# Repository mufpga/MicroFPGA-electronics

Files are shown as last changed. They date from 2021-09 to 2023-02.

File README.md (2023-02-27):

<a href="https://mufpga.github.io/">Overview

</a>



# Overview

MicroFPGA is an FPGA-based platform for the electronic control of microscopes. It aims at using affordable FPGA to generate or read signals from a variety of devices, including cameras, lasers, servomotors, filter-wheels, etc. It can be controlled via [Micro-Manager](https://micro-manager.org/MicroFPGA), or its [Java](https://github.com/mufpga/MicroFPGA-java), [Python](https://github.com/mufpga/MicroFPGA-py) and [LabView](https://github.com/mufpga/MicroFPGA-labview) communication libraries, and comes with optional complementary [electronics](https://github.com/mufpga/MicroFPGA-electronics).

Documentation and tutorials are available on [https://mufpga.github.io/](https://mufpga.github.io/).

Overview

## Content

This repository contains the (optional) complementary electronics for MicroFPGA. Documentation for the electronics is available on the [project's website](https://mufpga.github.io/resource1_electronics.html) and in the papers.

Design files are available for the following elements:
- [Box](Box)
- [Box panel 1](Box_panel_1)
- [Box panel 2](Box_panel_2)
- [Box panel 3](Box_panel_3)
- [Analog conversion board (ACB)](Analog_conversion_board)
- [Signal conversion board (SCB)](Signal_conversion_board)
- [Custom FPGA shield](FPGA_shield)
- [Servo distribution board (SDB)](Servo_distribution_board)
- [AOTF conversion board (AOTF-CB)](AOTF_conversion_board)

## Cite us
Joran Deschamps, Christian Kieser, Philipp Hoess, Takahiro Deguchi, Jonas Ries, "MicroFPGA: An affordable FPGA platform for microscope control",
HardwareX 2023 (13): e00407, doi:[10.1016/j.ohx.2023.e00407](https://doi.org/10.1016/j.ohx.2023.e00407).

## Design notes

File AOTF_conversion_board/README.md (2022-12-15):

<a href="https://mufpga.github.io/">Overview

</a>



## Content

The AOTF conversion board takes two TTL inputs per channels:
1. Enable in: a TTL trigger such as the one generated by MicroFPGA laser triggers or a camera exposure signal.
2. PWM or DAQ (analog in): a PWM signal such as the one generated by MicroFPGA PWM signals, or an analog signal.

The PWM signal is low-passed and the resulting analog output is multiplied by the TTL signal. The resulting output is a 10 V analog signal that can be synchronized with a camera, and whose level is adjusted by changing the PWM input duty cycle. The output of the board is either 0-5V or 0-10V depending on the channel.

We used this board in addition to our electronics box in order to control AOTF/AOM, for instance with DPSS lasers.

- [Altium project](Altium_project)
- [Bill of materials](BOM)
- [Gerber files](Gerber)
- [Drill instructions](NC_Drill)

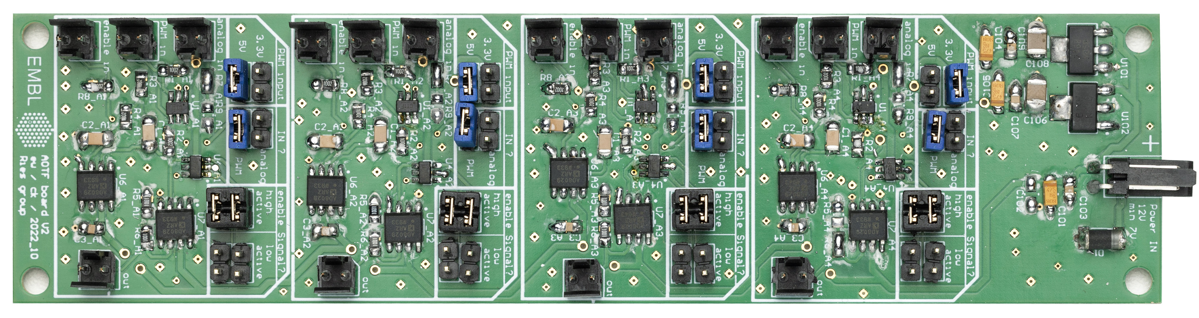
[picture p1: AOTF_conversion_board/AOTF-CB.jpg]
AOTF-CB


## Channel configuration

### Inputs
- _analog in_: analog signal that can be switched on or of by the _enable in_ signal.
- _PWM in_: PWM signal, which will be low-pass filtered by the board to generate an analog signal.
- _enable in_: TTL signal used to switch on and off the analog signal (_analog in_ or low-pass filtered _PWM in_)

> __Important__: inputs are either the analog or the PWM in, but not both simultaneously.
> Note: If you do not use the TTL input, you can set the _Enable signal ?_ to _low active_ in order to simply produce an analog signal.

### Ouput
- _out_: analog signal switched on/off following the TTL input.

### Settings
- _PWM input_: voltage of the PWM input (if applicable).
- _IN ?_: whether the input is _analog in_ or _PWM in_
- _Enable signal ?_: whether the analog output is switched on on _HIGH_ or _LOW_ TTL.

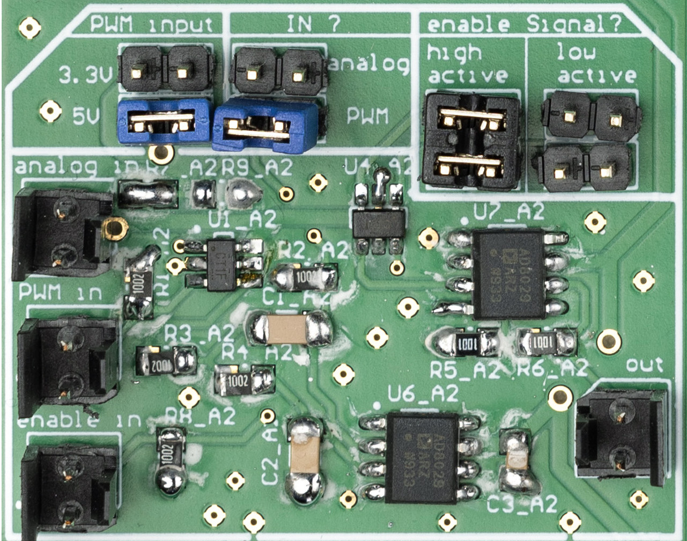
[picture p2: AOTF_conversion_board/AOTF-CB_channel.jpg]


Photography credit: EMBL Photolab - Stuart Ingham.

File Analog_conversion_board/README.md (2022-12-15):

<a href="https://mufpga.github.io/">Overview

</a>



## Content

The analog conversion board (ACB) scales down analog voltages from the ranges 0-10 V or 0-5 V to 0-1 V, in order to measure signals with the Au+ FPGA.

- [Altium project](Altium_project)
- [Bill of materials](BOM)
- [Gerber files](Gerber)
- [Drill instructions](NC_Drill)

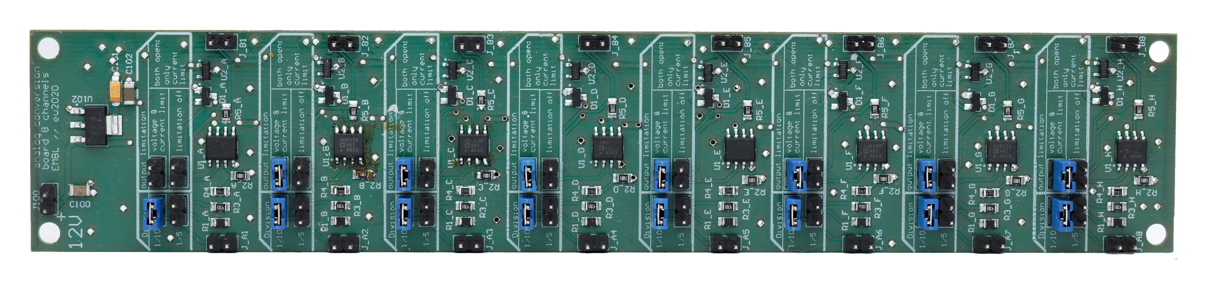
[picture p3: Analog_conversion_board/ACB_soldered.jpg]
ACB


## Channel configuration

### Input
- analog signal in the range 0-10V or 0-5V.

### Output
- analog signal in the range 0-1V.

### Settings
- _Division_: whether the input analog signal is 0-10V (1/10) or 0-5V (1/5), the output of the board is 0-1V.
- _output limitation_:
  - _voltage and current limitations_: limits both voltage and current to prevent damaging the FPGA ADC.
  - _limitations off_: the output voltage and current are not limited.
  - both open, only current limitation.

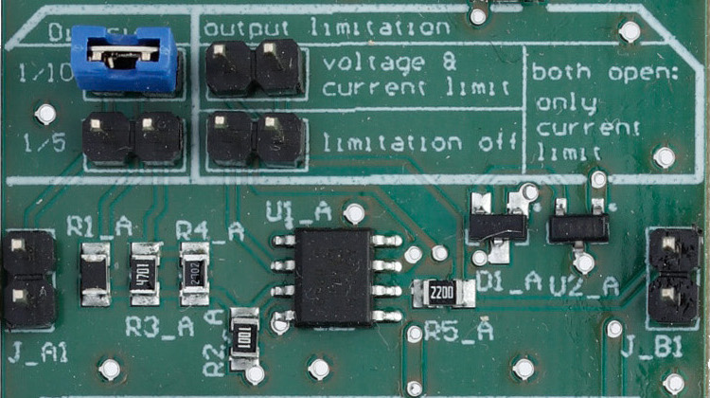
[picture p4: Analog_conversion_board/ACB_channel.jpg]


Photography credit: EMBL Photolab - Stuart Ingham.

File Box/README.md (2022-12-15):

<a href="https://mufpga.github.io/">Overview

</a>



## Content

The electronics box packages the different boards into a neat box with standard connectors. It is 3D printed and the lid machined from transparent plastic.

- [Bill of materials](BOM)
- [Build up pictures](Build_up)
- [CAD files](CAD_files)

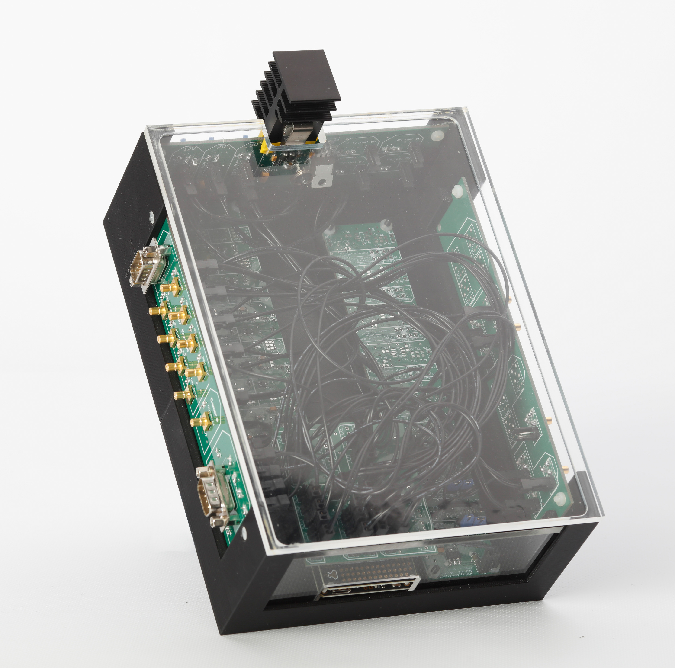
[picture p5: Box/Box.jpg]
Electronics box


Photography credit: EMBL Photolab - Stuart Ingham.

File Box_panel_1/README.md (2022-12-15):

<a href="https://mufpga.github.io/">Overview

</a>



## Content

The first box panel is connected to the laser (DO:LX:EN) and PWM signals (DO:LX:POW), as well as camera trigger input and the servos. The lasers outputs can be used directly to trigger diode lasers. The servo DSUB9 is connected to the [servo distribution board (SDB)](https://github.com/mufpga/MicroFPGA-electronics/tree/main/Servo_distribution_board). The other DSUB9 connector can be used with the [LaserEngine](https://github.com/ries-lab/LaserEngine) electronics. Finally, both laser and PWM signals could be used as inputs to the [AOTF conversion board (AOTF-CB)](https://github.com/mufpga/MicroFPGA-electronics/tree/main/AOTF_conversion_board) in order to control an AOTF or an AOM.

- [Altium project](Altium_project)
- [Bill of materials](BOM)
- [Gerber files](Gerber)
- [Drill instructions](NC_Drill)

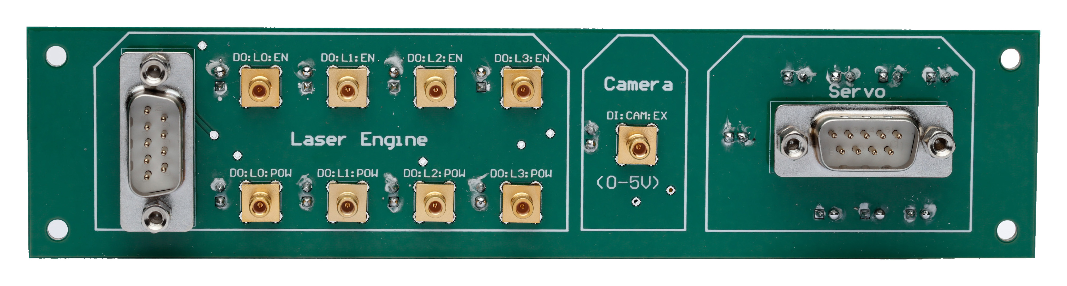
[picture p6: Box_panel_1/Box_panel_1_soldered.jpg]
Box panel 1


Photography credit: EMBL Photolab - Stuart Ingham.

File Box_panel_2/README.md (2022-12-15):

<a href="https://mufpga.github.io/">Overview

</a>



## Content

The second box panel is connected to AU+ analog inputs (in the case of the Cu FPGA, then these can be adapted for other outputs). It is also wired to the TTL outputs and the camera trigger output.

- [Altium project](Altium_project)
- [Bill of materials](BOM)
- [Gerber files](Gerber)
- [Drill instructions](NC_Drill)

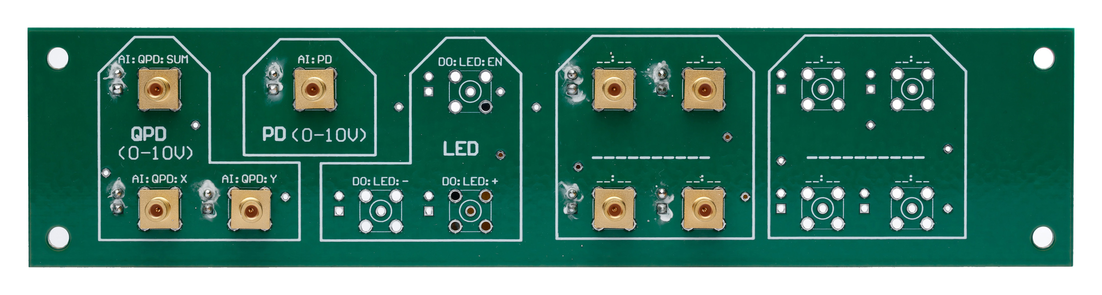
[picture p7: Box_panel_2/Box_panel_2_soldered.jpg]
Box panel 2


Photography credit: EMBL Photolab - Stuart Ingham.

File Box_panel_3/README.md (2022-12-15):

<a href="https://mufpga.github.io/">Overview

</a>



## Content

The third box panel is connected to the main power source and powers the other boards using different voltages.

- [Altium project](Altium_project)
- [Bill of materials](BOM)
- [Gerber files](Gerber)
- [Drill instructions](NC_Drill)

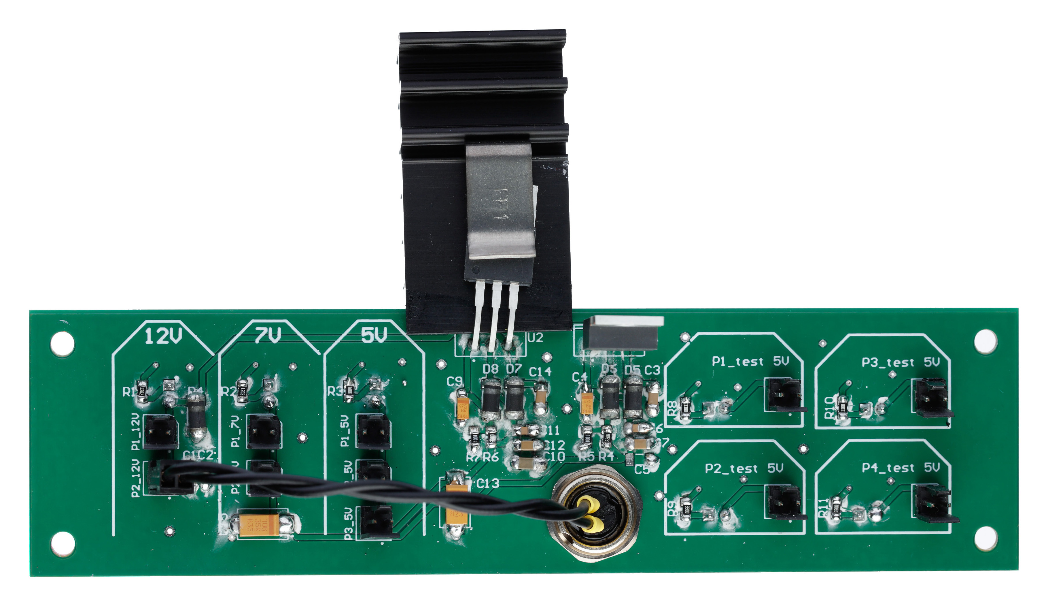
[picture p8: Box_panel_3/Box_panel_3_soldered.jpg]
Box panel 3


Photography credit: EMBL Photolab - Stuart Ingham.

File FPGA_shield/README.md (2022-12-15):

<a href="https://mufpga.github.io/">Overview

</a>



## Content

The custom FPGA shield can be plugged directly onto the Br shield (Alchitry) and facilitates the internal wiring of the electronics 
box. It features all the default inputs of MicroFPGA. Note that we prefer stacking it on top of the Br shield to avoid damaging the 
FPGA connectors and grant access to other FPGA pins that are unused by the custom shield.

- [Altium project](Altium_project)
- [Bill of materials](BOM)
- [Gerber files](Gerber)
- [Drill instructions](NC_Drill)

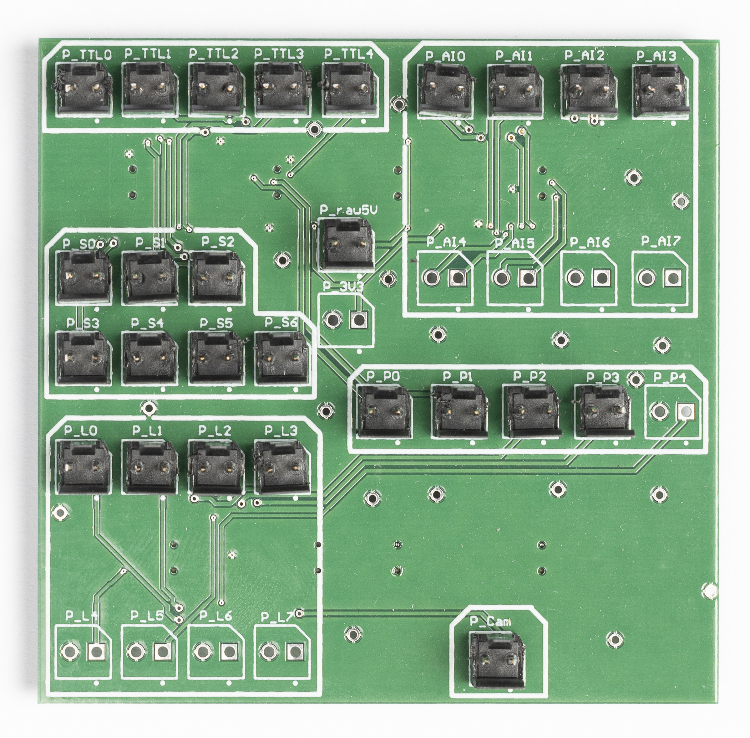
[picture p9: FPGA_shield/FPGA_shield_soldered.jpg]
Custom FPGA shield


Photography credit: EMBL Photolab - Stuart Ingham.

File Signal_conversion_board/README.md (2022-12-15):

<a href="https://mufpga.github.io/">Overview

</a>



## Content

The signal conversion board (SCB) features multiple bi-directional channels that scale up or down voltages in order to ensure compatibility
between the FPGA and devices connected to the electronics box. Two channels also include the possibility to low pass the PWM signals 
from MicroFPGA to produce analog voltage ouputs.

- [Altium project](Altium_project)
- [Bill of materials](BOM)
- [Gerber files](Gerber)
- [Drill instructions](NC_Drill)

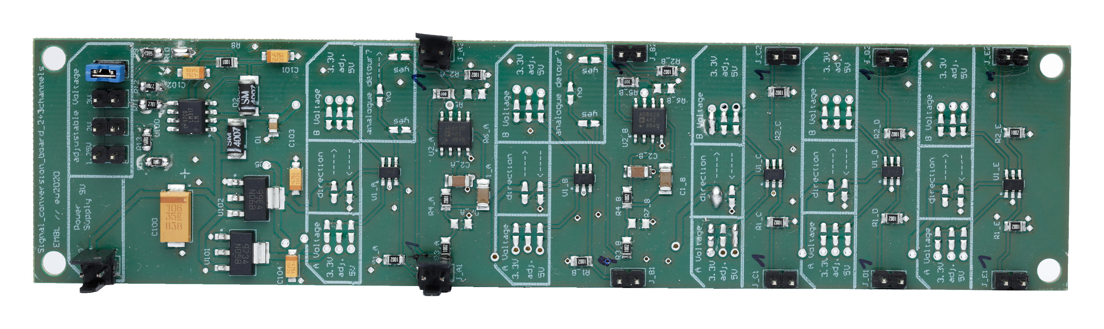
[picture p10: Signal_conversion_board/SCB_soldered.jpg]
SCB


## Channel configuration

Signal A on the left-hand side, signal B on the right-hand side.

### Input
- Digital signal (in A or B).

### Output
- Rescaled digital (in A or B) or analog signal (B).

### Settings
- _A voltage_: left-hand side voltage, where _adj_ is the adjustable voltage at the top of the board.
- _direction_: voltage conversion from left to right or right to left.
- _B voltage_: right-hand side voltage, where _adj_ is the adjustable voltage at the top of the board.
- _analogue detour_: whether to low pass A to produce an analog signal in B.
  
 > __Important__: digital to analog conversion (low-pass filter) only happens from A to B, from left to right.

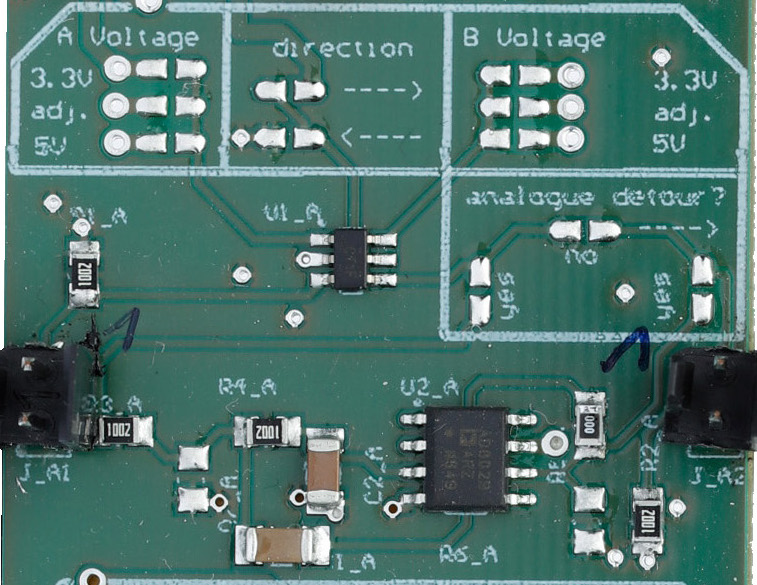
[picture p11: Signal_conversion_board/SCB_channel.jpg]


Photography credit: EMBL Photolab - Stuart Ingham.

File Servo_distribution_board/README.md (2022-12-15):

<a href="https://mufpga.github.io/">Overview

</a>



## Content

The servomotor distribution board (SDB) is intended to be a hub for servomotor cables. Placed in the center of the microscope, we use it to drive several servomotors (back-focal plane lens, 3D lens, filter wheels etc.), such as [the elements presented here](https://github.com/ries-lab/RiesPieces/tree/master/Microscopy). The flat cable from the DSUB9 is connected directly to the electronics box. It is simply screwed on a plastic board.

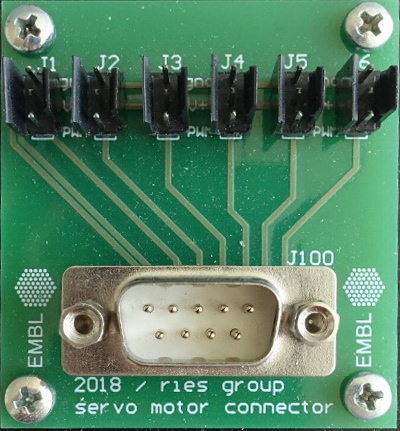
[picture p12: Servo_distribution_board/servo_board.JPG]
servomotor board


The project contains the following items:

- [Altium project](Altium_project)
- [Gerber files](Gerber)
- [Drill instructions](NC_Drill)

The board was designed by Ulf Matti (Ries lab, EMBL).

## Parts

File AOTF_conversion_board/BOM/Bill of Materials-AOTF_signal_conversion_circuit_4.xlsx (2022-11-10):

Line # | Name | Description | Designator | Revision ID | Quantity | Supplier | Supplier Part Number | PartNumber | Manufacturer
 | 61300211121 | 2Pol; gerade; WR-PHD 2.54 mm THT Pin Header | J1_A1, J1_A2, J1_A3, J1_A4, J2_A1, J2_A2, J2_A3, J2_A4, J3_A1, J3_A2, J3_A3, J3_A4, J4_A1, J4_A2, J4_A3, J4_A4, J5_A1, J5_A2, J5_A3, J5_A4, J6_A1, J6_A2, J6_A3, J6_A4, J7_A1, J7_A2, J7_A3, J7_A4, J8_A1, J8_A2, J8_A3, J8_A4 | CMP-001-0071-1 | 32 | Mouser | 710-61300211121 | 61300211121 | Wurth Electronics
 | 4,7 µF | 4,7 µF; 6V; Gr. A; T491A475K006AT | C101, C102, C104, C105 | CMP-001-0039-3 | 4 | Digi-Key | 399-9717-1-ND | T491A475K006AT | KEMET
 | LM1117IMP-3.3/NOPB | 800mA Low-Dropout Linear Regulator, 4-pin SOT-223, Pb-Free | U101 | CMP-00484-1 | 1 |  |  | LM1117IMP-3.3/NOPB | Texas Instruments
 | LM1117IMP-5.0/NOPB | 800mA Low-Dropout Linear Regulator, 4-pin SOT-223, Pb-Free | U102 | CMP-00485-1 | 1 |  |  | LM1117IMP-5.0/NOPB | Texas Instruments
 | SN74LVC1G3157 | Analoger Schalter Single SPDT(Wechsler) SOT23-6 | U4_A1, U4_A2, U4_A3, U4_A4 | CMP-001-0106-A.1 | 4 | Digi-Key | 74LVC1G3157DBVRE4-ND | SN74LVC1G3157DBVR | Texas Instruments
 | 885012208013 | CAP CER 1UF 10V X7R 1206 | C1_A1, C1_A2, C1_A3, C1_A4, C2_A1, C2_A2, C2_A3, C2_A4 | CMP-001-0138-A.1 | 8 | Digi-Key | 732-7685-1-ND | 885012208013 | Wurth Electronics Inc.
 | 100uF 6.3V 1210 | Ceramic Capacitor, Ceramic, 100uF, 6.3V | C106, C108 | CMP-001-0186-3 | 2 |  |  | 885012109004 | Wurth Electronics
 | 66100211722 | Intercom Male Shrouded Locking Header WR-WTB, THT, Right Angled, pitch 2.54 mm, 1 x 2 position | J100 | CMP-00524-A.1 | 1 |  |  | 66100211722 | Wurth Elektronik
 | LL4007 | LL4007; Vf 1,1V @ 1A, If = 1A | D1 | CMP-001-0049-2 | 1 | Farnell | 2677381 | LL4007G | TAIWAN SEMICONDUCTOR
 | AD8029ARZ | Single Channel RRIO Operational Amplifier, 125 MHz BW, 62 V/us SR, Industrial, 8-pin SOIC (R-8), Tube | U6_A1, U6_A2, U6_A3, U6_A4, U7_A1, U7_A2, U7_A3, U7_A4 | CMP-00480-1 | 8 |  |  | AD8029ARZ | Analog Devices
 | SN74LVC1T45DBVT | Single-Bit Dual-Supply Bus Transceiver with Configurable Voltage Translation and 3-State Outputs, DBV0006A, SMALL T&R | U1_A1, U1_A2, U1_A3, U1_A4 | CMP-00491-1 | 4 |  |  | SN74LVC1T45DBVT | Texas Instruments
 | 66100211622 | WR-WTB 2.54 mm Male Vertical Shrouded Header 2 Pins | J_A1, J_A2, J_A3, J_A4, J_B1, J_B2, J_B3, J_B4, J_C1, J_C2, J_C3, J_C4, J_D1, J_D2, J_D3, J_D4 | CMP-001-0161-A.3 | 16 | Digi-Key | 732-14102-ND | 66100211622 | Wurth Electronics
 |  | Generic parts with the format 0805 like resistances and capacities are not listed here!!.

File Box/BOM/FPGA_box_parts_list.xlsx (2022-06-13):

name | producer & producer parts number | Distributor | order number |  | amount | comment
board content of FPGA box:
Alchitry Au FPGA DEV-16527 | SparkFun DEV-16527 | mouser | 474-DEV-16527 |  | 1
Alchitry Br prototype shield | SparkFun DEV-16524 | mouser | 474-DEV-16524 |  | 1
boards pre assembled from company:
analog_conversion_board_8channels | Sigmann electronic Angebot: 2020-30170 |  |  | 197,14€ for 1pc 130,82€ each for min. 5pc 110,40€ each for min. 10pc | 1
signal_conversion_board_2+3channels | Sigmann electronic Angebot: 2020-30170 |  |  | 132,59€ for 1pc 67,28€ each for min. 5pc 51,41€ each for min. 10pc | 1
boards self-assembled:
FPGA_Au_shield | Q-print ----- |  |  | not assembled ordered | 1
FPGA_Frontpanel_1_V2 | Q-print ----- |  |  | not assembled ordered | 1
FPGA_Frontpanel_2_V1 | Q-print ----- |  |  | not assembled ordered | 1
FPGA_Frontpanel_3_V1 | Q-print ----- |  |  | not assembled ordered | 1
power supply
Mean Well Steckernetzteil Universal 12V dc / 1.5A, 18W | Mean Well GSM18E12-P1J | RS | 791-0913 |  | 1
cable connector 2 pole | Binder 99 0402 00 02 | Farnell | 1122556 |  | 1
box connector 2 pole | Binder 09 0403 00 02 | Farnell | 1122562 |  | 1
Box build up
spacing bolts, plastic, internal-|external-, M3 | M3, 10 mm long and 8mm outside |  | Bürklin | 18H3683 |  | 8 | beneath ACB and SCB boards
spacing bolts, metal, internal-|internal-, M2 | M2, 15 mm long |  | Bürklin | 18H2408 |  | 3 | beneath FPGA board
M4 nuts for distance holding |  |  |  |  | 3 | beneath FPGA board
M2 metal screws 10mm long with countersunk head |  |  |  |  | 3 | for FPGA board
M2 metal screws 12mm long with flat head |  |  |  |  | 3 | for FPGA board
M3 (plastic) screws 10mm long with countersunk head |  |  |  |  | 14 | for ACB/SCB and frontpanels
M3 (plastic) nut |  |  |  |  | 14 | for ACB/SCB and frontpanels
heat sink | Fischerelektronik THFU 1 | RS | 722-6921 |  | 1
heat sink clip | Fischerelektronik SK 481/25 SA | RS | 722-6886 |  | 1
2 x 1 PINS Multi-Jumper | Wuerth Electronic 60900213621 | Wuerth Electronic | 60900213621 |  | 16 | jumpers for the ACB board
WR-WTB from würth electronic prefabricated cables for wiring the boards
2 Pins | würth electronic | 661002113322 |  |  | 54 | current need but it depends on amount of signals needed
30cm both ends crimped | würth electronic | 661161122030 |  |  | 44 | current need but it depends on amount of signals needed

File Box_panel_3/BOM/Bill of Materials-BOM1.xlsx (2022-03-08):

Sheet: BOM Report
BOM Beta LAYOUT GmbH
 |  |  | Bill of Materials for BOM Document [BOM1.BomDoc]
Source Data From: |  | BOM1.BomDoc
Project: |  | FPGA_Frontpanel_3_V1.PrjPcb
Variant: |  | None
Creation Date: | 27.09.2021
Print Date: | 2021-09-27 | 44466.65563
Production Quantity: | 1
 |  |  |  |  |  |  |  |  |  |  |  | D | E | L |  | E | T | E
Designator | Name | LibRef | Footprint | Description | Quantity | Place YES / NO | Provided by Customer YES / NO | Supplier | Supplier Part Number | Manufacturer | PartNumber | Supplier 1 | Supplier Stock 1 | Supplier Part Number 1 | Supplier Order Qty 1 | Supplier Unit Price 1 | #Column Name Error:' Supplier 2 | #Column Name Error:' Supplier Stock 2 | #Column Name Error:' Supplier Part Number 2 | #Column Name Error:' Supplier Order Qty 2 | #Column Name Error:' Supplier Unit Price 2 | #Column Name Error:' Supplier 3 | #Column Name Error:' Supplier Stock 3 | #Column Name Error:' Supplier Part Number 3 | #Column Name Error:' Supplier Order Qty 3 | #Column Name Error:' Supplier Unit Price 3
J1 | 61300211121 | CMP-001-0071-2 | 61300211121 | 2Pol; gerade; WR-PHD 2.54 mm THT Pin Header | 1 | YES | NO | Mouser | 710-61300211121 | Wurth Electronics | 61300211121 | Mouser | 58866 | 710-61300211121 | 7 | 0.11
J2 | 61300211121 | CMP-001-0071-2 | 61300211121 | 2Pol; gerade; WR-PHD 2.54 mm THT Pin Header | 1 | YES | NO | Mouser | 710-61300211121 | Wurth Electronics | 61300211121 | Mouser | 58866 | 710-61300211121 | 7 | 0.11
J3 | 61300211121 | CMP-001-0071-2 | 61300211121 | 2Pol; gerade; WR-PHD 2.54 mm THT Pin Header | 1 | YES | NO | Mouser | 710-61300211121 | Wurth Electronics | 61300211121 | Mouser | 58866 | 710-61300211121 | 7 | 0.11
J4 | 61300211121 | CMP-001-0071-2 | 61300211121 | 2Pol; gerade; WR-PHD 2.54 mm THT Pin Header | 1 | YES | NO | Mouser | 710-61300211121 | Wurth Electronics | 61300211121 | Mouser | 58866 | 710-61300211121 | 7 | 0.11
J5 | 61300211121 | CMP-001-0071-2 | 61300211121 | 2Pol; gerade; WR-PHD 2.54 mm THT Pin Header | 1 | YES | NO | Mouser | 710-61300211121 | Wurth Electronics | 61300211121 | Mouser | 58866 | 710-61300211121 | 7 | 0.11
J6 | 61300211121 | CMP-001-0071-2 | 61300211121 | 2Pol; gerade; WR-PHD 2.54 mm THT Pin Header | 1 | YES | NO | Mouser | 710-61300211121 | Wurth Electronics | 61300211121 | Mouser | 58866 | 710-61300211121 | 7 | 0.11
J7 | 61300211121 | CMP-001-0071-2 | 61300211121 | 2Pol; gerade; WR-PHD 2.54 mm THT Pin Header | 1 | YES | NO | Mouser | 710-61300211121 | Wurth Electronics | 61300211121 | Mouser | 58866 | 710-61300211121 | 7 | 0.11
U1 | LM317AT/NOPB | CMP-00535-1 | NDE0003A | 3-Terminal Adjustable Regulator, 3-pin TO-220, Pb-Free | 1 | YES | NO |  |  | Texas Instruments |  | Mouser | 154 | 926-LM317AT/NOPB | 2 | 1.72
U2 | LM317AT/NOPB | CMP-00535-1 | NDE0003A | 3-Terminal Adjustable Regulator, 3-pin TO-220, Pb-Free | 1 | YES | NO |  |  | Texas Instruments |  | Mouser | 154 | 926-LM317AT/NOPB | 2 | 1.72
C4 | 4,7 µF | CMP-001-0039-5 | A Package | 4,7 µF; 6V; Gr. A; T491A475K006AT | 1 | YES | NO | Digi-Key | 399-9717-1-ND | KEMET | T491A475K006AT | Distrelec | 0 | 16771162 | 1 | 3.49
C9 | 4,7 µF | CMP-001-0039-3 | A Package | 4,7 µF; 6V; Gr. A; T491A475K006AT | 1 | YES | NO | Digi-Key | 399-9717-1-ND | KEMET | T491A475K006AT | Distrelec | 0 | 16771162 | 1 | 4.09
C13 | 10 µF | CMP-001-0033-3 | KEMT-520-D_Low | 10 µF, 35V, 125 mOhm, Gr. D partnumb: T495D106K035ATE125 | 1 | YES | NO | Digi-Key | 399-10292-1-ND | KEMET | T495D106K035ATE125 | Farnell | 441 | 2524590 | 2 | 3.5
C15 | 10 µF | CMP-001-0033-3 | KEMT-520-D_Low | 10 µF, 35V, 125 mOhm, Gr. D partnumb: T495D106K035ATE125 | 1 | YES | NO | Digi-Key | 399-10292-1-ND | KEMET | T495D106K035ATE125 | Farnell | 441 | 2524590 | 2 | 3.5
R1 | 805 | CMP-001-0027-2 | YAGO-RC0805_M | 0805 Yageo Standard BlackBox Resistors | 1 | YES | NO |  |  | Yageo
R2 | 805 | CMP-001-0027-2 | YAGO-RC0805_M | 0805 Yageo Standard BlackBox Resistors | 1 | YES | NO |  |  | Yageo
R3 | 805 | CMP-001-0027-2 | YAGO-RC0805_M | 0805 Yageo Standard BlackBox Resistors | 1 | YES | NO |  |  | Yageo
R4 | 805 | CMP-001-0027-2 | YAGO-RC0805_M | 0805 Yageo Standard BlackBox Resistors | 1 | YES | NO |  |  | Yageo
R5 | 805 | CMP-001-0027-2 | YAGO-RC0805_M | 0805 Yageo Standard BlackBox Resistors | 1 | YES | NO |  |  | Yageo
R6 | 805 | CMP-001-0027-2 | YAGO-RC0805_M | 0805 Yageo Standard BlackBox Resistors | 1 | YES | NO |  |  | Yageo
R7 | 805 | CMP-001-0027-2 | YAGO-RC0805_M | 0805 Yageo Standard BlackBox Resistors | 1 | YES | NO |  |  | Yageo
R8 | 805 | CMP-001-0027-2 | YAGO-RC0805_M | 0805 Yageo Standard BlackBox Resistors | 1 | YES | NO |  |  | Yageo
R9 | 805 | CMP-001-0027-2 | YAGO-RC0805_M | 0805 Yageo Standard BlackBox Resistors | 1 | YES | NO |  |  | Yageo
R10 | 805 | CMP-001-0027-2 | YAGO-RC0805_M | 0805 Yageo Standard BlackBox Resistors | 1 | YES | NO |  |  | Yageo
R11 | 805 | CMP-001-0027-2 | YAGO-RC0805_M | 0805 Yageo Standard BlackBox Resistors | 1 | YES | NO |  |  | Yageo
C3 | CAP 10uF 25V 1206(3216) | CMP-00471-2 | CAPC1206(3216)190_N | CAP 10uF 25V -20% to +80% 1206 (3216 Metric) Thickness 1.9mm SMD | 1 | YES | NO | Digi-Key | 732-7574-2-ND | Wurth Electronics Inc. | 885 012 208 069 | RSComponents | 25 | 1813519 | 25 | 0.54732
C5 | CAP 10uF 25V 1206(3216) | CMP-00471-2 | CAPC1206(3216)190_N | CAP 10uF 25V -20% to +80% 1206 (3216 Metric) Thickness 1.9mm SMD | 1 | YES | NO | Digi-Key | 732-7574-2-ND | Wurth Electronics Inc. | 885 012 208 069 | RSComponents | 25 | 1813519 | 25 | 0.54732
C10 | CAP 10uF 25V 1206(3216) | CMP-00471-2 | CAPC1206(3216)190_N | CAP 10uF 25V -20% to +80% 1206 (3216 Metric) Thickness 1.9mm SMD | 1 | YES | NO | Digi-Key | 732-7574-2-ND | Wurth Electronics Inc. | 885 012 208 069 | RSComponents | 25 | 1813519 | 25 | 0.54732
C14 | CAP 10uF 25V 1206(3216) | CMP-00471-2 | CAPC1206(3216)190_N | CAP 10uF 25V -20% to +80% 1206 (3216 Metric) Thickness 1.9mm SMD | 1 | YES | NO | Digi-Key | 732-7574-2-ND | Wurth Electronics Inc. | 885 012 208 069 | RSComponents | 25 | 1813519 | 25 | 0.54732
C1 | CAP 100uF 6.3V 1206(3216) | CMP-00469-2 | CAPC1206(3216)190_L | CAP 100uF 6.3V ±20% 1206 (3216 Metric) Thickness 1.9mm SMD | 1 | YES | NO | Farnell | 2495155 | WURTH ELEKTRONIK | 885012108005 | RSComponents | 5960 | 1813482 | 10 | 0.69734
C7 | CAP 100uF 6.3V 1206(3216) | CMP-00469-2 | CAPC1206(3216)190_L | CAP 100uF 6.3V ±20% 1206 (3216 Metric) Thickness 1.9mm SMD | 1 | YES | NO | Farnell | 2495155 | WURTH ELEKTRONIK | 885012108005 | RSComponents | 5960 | 1813482 | 10 | 0.69734
C12 | CAP 100uF 6.3V 1206(3216) | CMP-00469-2 | CAPC1206(3216)190_L | CAP 100uF 6.3V ±20% 1206 (3216 Metric) Thickness 1.9mm SMD | 1 | YES | NO | Farnell | 2495155 | WURTH ELEKTRONIK | 885012108005 | RSComponents | 5960 | 1813482 | 10 | 0.69734
C2 | 805 | CMP-001-0082-2 | CAPC2013X88X50ML20T25 | generic 0805 COG oder X7R Vielschichtkondensatoren max. +/-10% | 1 | YES | NO
C6 | 805 | CMP-001-0082-2 | CAPC2013X88X50ML20T25 | generic 0805 COG oder X7R Vielschichtkondensatoren max. +/-10% | 1 | YES | NO
C11 | 805 | CMP-001-0082-2 | CAPC2013X88X50ML20T25 | generic 0805 COG oder X7R Vielschichtkondensatoren max. +/-10% | 1 | YES | NO
D4 | LL4007 | CMP-001-0049-2 | LL4007 | LL4007; Vf 1,1V @ 1A, If = 1A | 1 | YES | NO | Farnell | 2677381 | TAIWAN SEMICONDUCTOR | LL4007G L2 | Distrelec | 0 | 17043151 | 5 | 0.12587
D5 | LL4007 | CMP-001-0049-2 | LL4007 | LL4007; Vf 1,1V @ 1A, If = 1A | 1 | YES | NO | Farnell | 2677381 | TAIWAN SEMICONDUCTOR | LL4007G L2 | Distrelec | 0 | 17043151 | 5 | 0.12587
D6 | LL4007 | CMP-001-0049-2 | LL4007 | LL4007; Vf 1,1V @ 1A, If = 1A | 1 | YES | NO | Farnell | 2677381 | TAIWAN SEMICONDUCTOR | LL4007G L2 | Distrelec | 0 | 17043151 | 5 | 0.12587
D7 | LL4007 | CMP-001-0049-2 | LL4007 | LL4007; Vf 1,1V @ 1A, If = 1A | 1 | YES | NO | Farnell | 2677381 | TAIWAN SEMICONDUCTOR | LL4007G L2 | Distrelec | 0 | 17043151 | 5 | 0.12587
D8 | LL4007 | CMP-001-0049-2 | LL4007 | LL4007; Vf 1,1V @ 1A, If = 1A | 1 | YES | NO | Farnell | 2677381 | TAIWAN SEMICONDUCTOR | LL4007G L2 | Distrelec | 0 | 17043151 | 5 | 0.12587
D9 | 155124GS73200 | CMP-001-0164-1 | 1204 | Single Color LED, Green, Water Clear, 2mm | 1 | YES | NO |  |  |  |  | Farnell | 4278 | 2322100 | 3 | 0.52857
D10 | 155124GS73200 | CMP-001-0164-1 | 1204 | Single Color LED, Green, Water Clear, 2mm | 1 | YES | NO |  |  |  |  | Farnell | 4278 | 2322100 | 3 | 0.52857
D11 | 155124GS73200 | CMP-001-0164-1 | 1204 | Single Color LED, Green, Water Clear, 2mm | 1 | YES | NO |  |  |  |  | Farnell | 4278 | 2322100 | 3 | 0.52857
D12 | 155124YS73200 | CMP-00543-1 | 1204 | Single Color LED, Yellow, Water Clear, 2mm | 1 | YES | NO |  |  |  |  | Farnell | 2836 | 2322103 | 5 | 0.23206
D13 | 155124YS73200 | CMP-00543-1 | 1204 | Single Color LED, Yellow, Water Clear, 2mm | 1 | YES | NO |  |  |  |  | Farnell | 2836 | 2322103 | 5 | 0.23206
D14 | 155124YS73200 | CMP-00543-1 | 1204 | Single Color LED, Yellow, Water Clear, 2mm | 1 | YES | NO |  |  |  |  | Farnell | 2836 | 2322103 | 5 | 0.23206
D15 | 155124YS73200 | CMP-00543-1 | 1204 | Single Color LED, Yellow, Water Clear, 2mm | 1 | YES | NO |  |  |  |  | Farnell | 2836 | 2322103 | 5 | 0.23206
P1_5V | 66100211622 | CMP-001-0161-A.3 | 66100211622 | WR-WTB 2.54 mm Male Vertical Shrouded Header 2 Pins | 1 | YES | NO | Digi-Key | 732-14102-ND | Wurth Electronics | 66100211622 | Distrelec | 57 | 30213014 | 11 | 0.36332
P1_7V | 66100211622 | CMP-001-0161-A.3 | 66100211622 | WR-WTB 2.54 mm Male Vertical Shrouded Header 2 Pins | 1 | YES | NO | Digi-Key | 732-14102-ND | Wurth Electronics | 66100211622 | Distrelec | 57 | 30213014 | 11 | 0.36332
P1_12V | 66100211622 | CMP-001-0161-A.3 | 66100211622 | WR-WTB 2.54 mm Male Vertical Shrouded Header 2 Pins | 1 | YES | NO | Digi-Key | 732-14102-ND | Wurth Electronics | 66100211622 | Distrelec | 57 | 30213014 | 11 | 0.36332
P1_test 5V | 66100211622 | CMP-001-0161-A.3 | 66100211622 | WR-WTB 2.54 mm Male Vertical Shrouded Header 2 Pins | 1 | YES | NO | Digi-Key | 732-14102-ND | Wurth Electronics | 66100211622 | Distrelec | 57 | 30213014 | 11 | 0.36332
P2_5V | 66100211622 | CMP-001-0161-A.3 | 66100211622 | WR-WTB 2.54 mm Male Vertical Shrouded Header 2 Pins | 1 | YES | NO | Digi-Key | 732-14102-ND | Wurth Electronics | 66100211622 | Distrelec | 57 | 30213014 | 11 | 0.36332
P2_7V | 66100211622 | CMP-001-0161-A.3 | 66100211622 | WR-WTB 2.54 mm Male Vertical Shrouded Header 2 Pins | 1 | YES | NO | Digi-Key | 732-14102-ND | Wurth Electronics | 66100211622 | Distrelec | 57 | 30213014 | 11 | 0.36332
P2_12V | 66100211622 | CMP-001-0161-A.3 | 66100211622 | WR-WTB 2.54 mm Male Vertical Shrouded Header 2 Pins | 1 | YES | NO | Digi-Key | 732-14102-ND | Wurth Electronics | 66100211622 | Distrelec | 57 | 30213014 | 11 | 0.36332
P2_test 5V | 66100211622 | CMP-001-0161-A.3 | 66100211622 | WR-WTB 2.54 mm Male Vertical Shrouded Header 2 Pins | 1 | YES | NO | Digi-Key | 732-14102-ND | Wurth Electronics | 66100211622 | Distrelec | 57 | 30213014 | 11 | 0.36332
P3_5V | 66100211622 | CMP-001-0161-A.3 | 66100211622 | WR-WTB 2.54 mm Male Vertical Shrouded Header 2 Pins | 1 | YES | NO | Digi-Key | 732-14102-ND | Wurth Electronics | 66100211622 | Distrelec | 57 | 30213014 | 11 | 0.36332
P3_test 5V | 66100211622 | CMP-001-0161-A.3 | 66100211622 | WR-WTB 2.54 mm Male Vertical Shrouded Header 2 Pins | 1 | YES | NO | Digi-Key | 732-14102-ND | Wurth Electronics | 66100211622 | Distrelec | 57 | 30213014 | 11 | 0.36332
P4_test 5V | 66100211622 | CMP-001-0161-A.3 | 66100211622 | WR-WTB 2.54 mm Male Vertical Shrouded Header 2 Pins | 1 | YES | NO | Digi-Key | 732-14102-ND | Wurth Electronics | 66100211622 | Distrelec | 57 | 30213014 | 11 | 0.36332
 |  |  |  |  |  | YES | NO
 |  |  |  |  |  | YES | NO

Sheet: Project Information
Project Full Path | Free Documents
Project Filename | Free Documents
Variant Name | None
Data-Source Filename | BS50602e3f4ab07_UniAdc_pcbpool_20120924115706.PcbDoc
Data-Source Full Path | U:\Job\BA\Altium Testfile\BS50602e3f4ab07_UniAdc_pcbpool_20120924115706.PcbDoc
Title | Bill of Materials For PCB Document [BS50602e3f4ab07_UniAdc_pcbpool_20120924115706.PcbDoc]
Total Quantity | 55
Report Time | 10:07:24
Report Date | 16.10.2012
Report Date & Tine | 16.10.2012 10:07:24
Output Name | Bill of Materials
Output Type | BOM_PartType
Output Generator Name | ReportComponents
Output Generator Description | Component Reports

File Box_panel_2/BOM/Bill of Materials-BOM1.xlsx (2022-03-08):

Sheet: BOM Report
BOM Beta LAYOUT GmbH
 |  |  | Bill of Materials for BOM Document [BOM1.BomDoc]
Source Data From: |  | BOM1.BomDoc
Project: |  | FPGA_Frontpanel_2_V2.PrjPcb
Variant: |  | None
Creation Date: | 27.09.2021
Print Date: | 2021-09-27 | 44466.64795
Production Quantity: | 1
 |  |  |  |  |  |  |  |  |  |  |  | D | E | L |  | E | T | E
Designator | Name | LibRef | Footprint | Description | Quantity | Place YES / NO | Provided by Customer YES / NO | Supplier | Supplier Part Number | Manufacturer | PartNumber | Supplier 1 | Supplier Stock 1 | Supplier Part Number 1 | Supplier Order Qty 1 | Supplier Unit Price 1 | #Column Name Error:' Supplier 2 | #Column Name Error:' Supplier Stock 2 | #Column Name Error:' Supplier Part Number 2 | #Column Name Error:' Supplier Order Qty 2 | #Column Name Error:' Supplier Unit Price 2 | #Column Name Error:' Supplier 3 | #Column Name Error:' Supplier Stock 3 | #Column Name Error:' Supplier Part Number 3 | #Column Name Error:' Supplier Order Qty 3 | #Column Name Error:' Supplier Unit Price 3
AI:PD | J01160A0211 | CMP-00545-1 | J01160A0211 | RF SMB Connector, Male, Board Mount, Solder Terminal, Receptacle | 1 | YES | NO |  |  |  |  | RSComponents | 1 | 3098505 | 0 | 0
AI:QPD:SUM | J01160A0211 | CMP-00545-1 | J01160A0211 | RF SMB Connector, Male, Board Mount, Solder Terminal, Receptacle | 1 | YES | NO |  |  |  |  | RSComponents | 1 | 3098505 | 0 | 0
AI:QPD:X | J01160A0211 | CMP-00545-1 | J01160A0211 | RF SMB Connector, Male, Board Mount, Solder Terminal, Receptacle | 1 | YES | NO |  |  |  |  | RSComponents | 1 | 3098505 | 0 | 0
AI:QPD:Y | J01160A0211 | CMP-00545-1 | J01160A0211 | RF SMB Connector, Male, Board Mount, Solder Terminal, Receptacle | 1 | YES | NO |  |  |  |  | RSComponents | 1 | 3098505 | 0 | 0
DO:LED:- | J01160A0211 | CMP-00545-1 | J01160A0211 | RF SMB Connector, Male, Board Mount, Solder Terminal, Receptacle | 1 | YES | NO |  |  |  |  | RSComponents | 1 | 3098505 | 0 | 0
DO:LED:+ | J01160A0211 | CMP-00545-1 | J01160A0211 | RF SMB Connector, Male, Board Mount, Solder Terminal, Receptacle | 1 | YES | NO |  |  |  |  | RSComponents | 1 | 3098505 | 0 | 0
DO:LED:EN | J01160A0211 | CMP-00545-1 | J01160A0211 | RF SMB Connector, Male, Board Mount, Solder Terminal, Receptacle | 1 | YES | NO |  |  |  |  | RSComponents | 1 | 3098505 | 0 | 0
J8_1 | J01160A0211 | CMP-00545-1 | J01160A0211 | RF SMB Connector, Male, Board Mount, Solder Terminal, Receptacle | 1 | YES | NO |  |  |  |  | RSComponents | 1 | 3098505 | 0 | 0
J9_1 | J01160A0211 | CMP-00545-1 | J01160A0211 | RF SMB Connector, Male, Board Mount, Solder Terminal, Receptacle | 1 | YES | NO |  |  |  |  | RSComponents | 1 | 3098505 | 0 | 0
J10_1 | J01160A0211 | CMP-00545-1 | J01160A0211 | RF SMB Connector, Male, Board Mount, Solder Terminal, Receptacle | 1 | YES | NO |  |  |  |  | RSComponents | 1 | 3098505 | 0 | 0
J11_1 | J01160A0211 | CMP-00545-1 | J01160A0211 | RF SMB Connector, Male, Board Mount, Solder Terminal, Receptacle | 1 | YES | NO |  |  |  |  | RSComponents | 1 | 3098505 | 0 | 0
J12_1 | J01160A0211 | CMP-00545-1 | J01160A0211 | RF SMB Connector, Male, Board Mount, Solder Terminal, Receptacle | 1 | YES | NO |  |  |  |  | RSComponents | 1 | 3098505 | 0 | 0
J13_1 | J01160A0211 | CMP-00545-1 | J01160A0211 | RF SMB Connector, Male, Board Mount, Solder Terminal, Receptacle | 1 | YES | NO |  |  |  |  | RSComponents | 1 | 3098505 | 0 | 0
J14_1 | J01160A0211 | CMP-00545-1 | J01160A0211 | RF SMB Connector, Male, Board Mount, Solder Terminal, Receptacle | 1 | YES | NO |  |  |  |  | RSComponents | 1 | 3098505 | 0 | 0
J15_1 | J01160A0211 | CMP-00545-1 | J01160A0211 | RF SMB Connector, Male, Board Mount, Solder Terminal, Receptacle | 1 | YES | NO |  |  |  |  | RSComponents | 1 | 3098505 | 0 | 0
J1 | 66100211622 | CMP-001-0161-A.3 | 66100211622 | WR-WTB 2.54 mm Male Vertical Shrouded Header 2 Pins | 1 | YES | NO | Digi-Key | 732-14102-ND | Wurth Electronics | 66100211622 | Distrelec | 57 | 30213014 | 15 | 0.36332
J2 | 66100211622 | CMP-001-0161-A.3 | 66100211622 | WR-WTB 2.54 mm Male Vertical Shrouded Header 2 Pins | 1 | YES | NO | Digi-Key | 732-14102-ND | Wurth Electronics | 66100211622 | Distrelec | 57 | 30213014 | 15 | 0.36332
J3 | 66100211622 | CMP-001-0161-A.3 | 66100211622 | WR-WTB 2.54 mm Male Vertical Shrouded Header 2 Pins | 1 | YES | NO | Digi-Key | 732-14102-ND | Wurth Electronics | 66100211622 | Distrelec | 57 | 30213014 | 15 | 0.36332
J4 | 66100211622 | CMP-001-0161-A.3 | 66100211622 | WR-WTB 2.54 mm Male Vertical Shrouded Header 2 Pins | 1 | YES | NO | Digi-Key | 732-14102-ND | Wurth Electronics | 66100211622 | Distrelec | 57 | 30213014 | 15 | 0.36332
J5 | 66100211622 | CMP-001-0161-A.3 | 66100211622 | WR-WTB 2.54 mm Male Vertical Shrouded Header 2 Pins | 1 | YES | NO | Digi-Key | 732-14102-ND | Wurth Electronics | 66100211622 | Distrelec | 57 | 30213014 | 15 | 0.36332
J6 | 66100211622 | CMP-001-0161-A.3 | 66100211622 | WR-WTB 2.54 mm Male Vertical Shrouded Header 2 Pins | 1 | YES | NO | Digi-Key | 732-14102-ND | Wurth Electronics | 66100211622 | Distrelec | 57 | 30213014 | 15 | 0.36332
J7 | 66100211622 | CMP-001-0161-A.3 | 66100211622 | WR-WTB 2.54 mm Male Vertical Shrouded Header 2 Pins | 1 | YES | NO | Digi-Key | 732-14102-ND | Wurth Electronics | 66100211622 | Distrelec | 57 | 30213014 | 15 | 0.36332
J8 | 66100211622 | CMP-001-0161-A.3 | 66100211622 | WR-WTB 2.54 mm Male Vertical Shrouded Header 2 Pins | 1 | YES | NO | Digi-Key | 732-14102-ND | Wurth Electronics | 66100211622 | Distrelec | 57 | 30213014 | 15 | 0.36332
J9 | 66100211622 | CMP-001-0161-A.3 | 66100211622 | WR-WTB 2.54 mm Male Vertical Shrouded Header 2 Pins | 1 | YES | NO | Digi-Key | 732-14102-ND | Wurth Electronics | 66100211622 | Distrelec | 57 | 30213014 | 15 | 0.36332
J10 | 66100211622 | CMP-001-0161-A.3 | 66100211622 | WR-WTB 2.54 mm Male Vertical Shrouded Header 2 Pins | 1 | YES | NO | Digi-Key | 732-14102-ND | Wurth Electronics | 66100211622 | Distrelec | 57 | 30213014 | 15 | 0.36332
J11 | 66100211622 | CMP-001-0161-A.3 | 66100211622 | WR-WTB 2.54 mm Male Vertical Shrouded Header 2 Pins | 1 | YES | NO | Digi-Key | 732-14102-ND | Wurth Electronics | 66100211622 | Distrelec | 57 | 30213014 | 15 | 0.36332
J12 | 66100211622 | CMP-001-0161-A.3 | 66100211622 | WR-WTB 2.54 mm Male Vertical Shrouded Header 2 Pins | 1 | YES | NO | Digi-Key | 732-14102-ND | Wurth Electronics | 66100211622 | Distrelec | 57 | 30213014 | 15 | 0.36332
J13 | 66100211622 | CMP-001-0161-A.3 | 66100211622 | WR-WTB 2.54 mm Male Vertical Shrouded Header 2 Pins | 1 | YES | NO | Digi-Key | 732-14102-ND | Wurth Electronics | 66100211622 | Distrelec | 57 | 30213014 | 15 | 0.36332
J14 | 66100211622 | CMP-001-0161-A.3 | 66100211622 | WR-WTB 2.54 mm Male Vertical Shrouded Header 2 Pins | 1 | YES | NO | Digi-Key | 732-14102-ND | Wurth Electronics | 66100211622 | Distrelec | 57 | 30213014 | 15 | 0.36332
J15 | 66100211622 | CMP-001-0161-A.3 | 66100211622 | WR-WTB 2.54 mm Male Vertical Shrouded Header 2 Pins | 1 | YES | NO | Digi-Key | 732-14102-ND | Wurth Electronics | 66100211622 | Distrelec | 57 | 30213014 | 15 | 0.36332
 |  |  |  |  |  | YES | NO
 |  |  |  |  |  | YES | NO

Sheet: Project Information
Project Full Path | Free Documents
Project Filename | Free Documents
Variant Name | None
Data-Source Filename | BS50602e3f4ab07_UniAdc_pcbpool_20120924115706.PcbDoc
Data-Source Full Path | U:\Job\BA\Altium Testfile\BS50602e3f4ab07_UniAdc_pcbpool_20120924115706.PcbDoc
Title | Bill of Materials For PCB Document [BS50602e3f4ab07_UniAdc_pcbpool_20120924115706.PcbDoc]
Total Quantity | 55
Report Time | 10:07:24
Report Date | 16.10.2012
Report Date & Tine | 16.10.2012 10:07:24
Output Name | Bill of Materials
Output Type | BOM_PartType
Output Generator Name | ReportComponents
Output Generator Description | Component Reports

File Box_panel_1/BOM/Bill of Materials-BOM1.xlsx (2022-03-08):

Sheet: BOM Report
BOM Beta LAYOUT GmbH
 |  |  | Bill of Materials for BOM Document [BOM1.BomDoc]
Source Data From: |  | BOM1.BomDoc
Project: |  | FPGA_Frontpanel_1_V2.PrjPcb
Variant: |  | None
Creation Date: | 27.09.2021
Print Date: | 2021-09-27 | 44466.64424
Production Quantity: | 1
 |  |  |  |  |  |  |  |  |  |  |  | D | E | L |  | E | T | E
Designator | Name | LibRef | Footprint | Description | Quantity | Place YES / NO | Provided by Customer YES / NO | Supplier | Supplier Part Number | Manufacturer | PartNumber | Supplier 1 | Supplier Stock 1 | Supplier Part Number 1 | Supplier Order Qty 1 | Supplier Unit Price 1 | #Column Name Error:' Supplier 2 | #Column Name Error:' Supplier Stock 2 | #Column Name Error:' Supplier Part Number 2 | #Column Name Error:' Supplier Order Qty 2 | #Column Name Error:' Supplier Unit Price 2 | #Column Name Error:' Supplier 3 | #Column Name Error:' Supplier Stock 3 | #Column Name Error:' Supplier Part Number 3 | #Column Name Error:' Supplier Order Qty 3 | #Column Name Error:' Supplier Unit Price 3
J18, J_LaserEngine | 61800929221 | CMP-001-0130-A.1 | PCBComponent | 61800929221 / 9pol | 2 | YES | NO |  |  |  | 61800929221
__:__:__, __:__:__?, DI:CAM:EX, DO:L0:EN, DO:L0:POW, DO:L1:EN, DO:L1:POW, DO:L2:EN, DO:L2:POW, DO:L3:EN, DO:L3:POW | J01160A0211 | CMP-00545-1 | J01160A0211 | RF SMB Connector, Male, Board Mount, Solder Terminal, Receptacle | 13 | YES | NO |  |  |  |  | RSComponents | 1 | 3098505 | 0 | 0
5V, J5, J6, J7, J8, J9, J10, J11, J12, J13, J14, J15, J16, J17, P_S0, P_S1, P_S2, P_S3, P_S4, P_S5, P_S6 | 66100211622 | CMP-001-0161-A.3 | 66100211622 | WR-WTB 2.54 mm Male Vertical Shrouded Header 2 Pins | 21 | YES | NO | Digi-Key | 732-14102-ND | Wurth Electronics | 66100211622 | Distrelec | 57 | 30213014 | 25 | 0.28128
 |  |  |  |  |  | YES | NO
 |  |  |  |  |  | YES | NO

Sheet: Project Information
Project Full Path | Free Documents
Project Filename | Free Documents
Variant Name | None
Data-Source Filename | BS50602e3f4ab07_UniAdc_pcbpool_20120924115706.PcbDoc
Data-Source Full Path | U:\Job\BA\Altium Testfile\BS50602e3f4ab07_UniAdc_pcbpool_20120924115706.PcbDoc
Title | Bill of Materials For PCB Document [BS50602e3f4ab07_UniAdc_pcbpool_20120924115706.PcbDoc]
Total Quantity | 55
Report Time | 10:07:24
Report Date | 16.10.2012
Report Date & Tine | 16.10.2012 10:07:24
Output Name | Bill of Materials
Output Type | BOM_PartType
Output Generator Name | ReportComponents
Output Generator Description | Component Reports

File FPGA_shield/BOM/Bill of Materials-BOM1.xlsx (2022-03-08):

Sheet: BOM Report
BOM Beta LAYOUT GmbH
 |  |  | Bill of Materials for BOM Document [BOM1.BomDoc]
Source Data From: |  | BOM1.BomDoc
Project: |  | FPGA_Au_shield.PrjPcb
Variant: |  | None
Creation Date: | 27.09.2021
Print Date: | 2021-09-27 | 44466.64053
Production Quantity: | 1
 |  |  |  |  |  |  |  |  |  |  |  | D | E | L |  | E | T | E
Designator | Name | LibRef | Footprint | Description | Quantity | Place YES / NO | Provided by Customer YES / NO | Supplier | Supplier Part Number | Manufacturer | PartNumber | Supplier 1 | Supplier Stock 1 | Supplier Part Number 1 | Supplier Order Qty 1 | Supplier Unit Price 1 | #Column Name Error:' Supplier 2 | #Column Name Error:' Supplier Stock 2 | #Column Name Error:' Supplier Part Number 2 | #Column Name Error:' Supplier Order Qty 2 | #Column Name Error:' Supplier Unit Price 2 | #Column Name Error:' Supplier 3 | #Column Name Error:' Supplier Stock 3 | #Column Name Error:' Supplier Part Number 3 | #Column Name Error:' Supplier Order Qty 3 | #Column Name Error:' Supplier Unit Price 3
Bank_A, Bank_B, Bank_C, Bank_D | 16890 | CMP-00541-6 | SSOP50P500X600-50N | Board to Board Double Slot Femal 50 PIN | 4 | YES | NO |  |  | Sparkfun | PRT-16890 | Digi-Key | 0 | 1568-PRT-16890-ND | 0 | 0
P_3V3, P_AI0, P_AI1, P_AI2, P_AI3, P_AI4, P_AI5, P_AI6, P_AI7, P_Cam, P_L0, P_L1, P_L2, P_L3, P_L4, P_L5, P_L6, P_L7, P_P0, P_P1, P_P2, P_P3, P_P4, P_raw5V, P_S0, P_S1, P_S2, P_S3, P_S4, P_S5, P_S6, P_TTL0, P_TTL1, P_TTL2, P_TTL3, P_TTL4 | 66100211622 | CMP-001-0161-A.3 | 66100211622 | WR-WTB 2.54 mm Male Vertical Shrouded Header 2 Pins | 36 | YES | NO | Digi-Key | 732-14102-ND | Wurth Electronics | 66100211622 | Distrelec | 57 | 30213014 | 36 | 0.28128
 |  |  |  |  |  | YES | NO
 |  |  |  |  |  | YES | NO
 |  |  |  |  |  | YES | NO

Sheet: Project Information
Project Full Path | Free Documents
Project Filename | Free Documents
Variant Name | None
Data-Source Filename | BS50602e3f4ab07_UniAdc_pcbpool_20120924115706.PcbDoc
Data-Source Full Path | U:\Job\BA\Altium Testfile\BS50602e3f4ab07_UniAdc_pcbpool_20120924115706.PcbDoc
Title | Bill of Materials For PCB Document [BS50602e3f4ab07_UniAdc_pcbpool_20120924115706.PcbDoc]
Total Quantity | 55
Report Time | 10:07:24
Report Date | 16.10.2012
Report Date & Tine | 16.10.2012 10:07:24
Output Name | Bill of Materials
Output Type | BOM_PartType
Output Generator Name | ReportComponents
Output Generator Description | Component Reports

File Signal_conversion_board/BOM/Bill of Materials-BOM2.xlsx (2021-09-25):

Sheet: BOM Report
BOM Beta LAYOUT GmbH
 |  |  | <Parameter Title not found>
Source Data From: |  | BOM2.BomDoc
Project: |  | signal_conversion_board_2+3channels.PrjPcb
Variant: |  | None
Creation Date: | 24.11.2020
Print Date: | 2020-11-24 | 44159.75249
Production Quantity: | 1
 |  |  |  |  |  |  |  |  |  |  |  | D | E | L |  | E | T | E
Designator | Comment | #Column Name Error:LibRef | #Column Name Error:Footprint | Description | Quantity | Place YES / NO | Provided by Customer YES / NO | Supplier | Supplier Part Number | Manufacturer | PartNumber | Supplier 1 | Supplier Stock 1 | Supplier Part Number 1 | Supplier Order Qty 1 | Supplier Unit Price 1 | #Column Name Error:Supplier 2 | #Column Name Error:Supplier Stock 2 | #Column Name Error:Supplier Part Number 2 | #Column Name Error:Supplier Order Qty 2 | #Column Name Error:Supplier Unit Price 2 | #Column Name Error:Supplier 3 | #Column Name Error:Supplier Stock 3 | #Column Name Error:Supplier Part Number 3 | #Column Name Error:Supplier Order Qty 3 | #Column Name Error:Supplier Unit Price 3
1.25V | 61300211121 |  |  | 2Pol; gerade; WR-PHD 2.54 mm THT Pin Header | 1 | YES | NO | Mouser | 710-61300211121 | Wurth Electronics | 61300211121 | Mouser | 30823 | 710-61300211121 (https://octopart-clicks.com/click/altium?manufacturer=Wurth%20Electronics&mpn=61300211121&seller=Mouser&sku=710-61300211121&country=DE&channel=BOM%20Report) | 1 | 0,13
2V | 61300211121 |  |  | 2Pol; gerade; WR-PHD 2.54 mm THT Pin Header | 1 | YES | NO | Mouser | 710-61300211121 | Wurth Electronics | 61300211121 | Mouser | 30823 | 710-61300211121 (https://octopart-clicks.com/click/altium?manufacturer=Wurth%20Electronics&mpn=61300211121&seller=Mouser&sku=710-61300211121&country=DE&channel=BOM%20Report) | 1 | 0,13
3V | 61300211121 |  |  | 2Pol; gerade; WR-PHD 2.54 mm THT Pin Header | 1 | YES | NO | Mouser | 710-61300211121 | Wurth Electronics | 61300211121 | Mouser | 30823 | 710-61300211121 (https://octopart-clicks.com/click/altium?manufacturer=Wurth%20Electronics&mpn=61300211121&seller=Mouser&sku=710-61300211121&country=DE&channel=BOM%20Report) | 1 | 0,13
4V | 61300211121 |  |  | 2Pol; gerade; WR-PHD 2.54 mm THT Pin Header | 1 | YES | NO | Mouser | 710-61300211121 | Wurth Electronics | 61300211121 | Mouser | 30823 | 710-61300211121 (https://octopart-clicks.com/click/altium?manufacturer=Wurth%20Electronics&mpn=61300211121&seller=Mouser&sku=710-61300211121&country=DE&channel=BOM%20Report) | 1 | 0,13
J100 | 61300211121 |  |  | 2Pol; gerade; WR-PHD 2.54 mm THT Pin Header | 1 | YES | NO | Mouser | 710-61300211121 | Wurth Electronics | 61300211121 | Mouser | 30823 | 710-61300211121 (https://octopart-clicks.com/click/altium?manufacturer=Wurth%20Electronics&mpn=61300211121&seller=Mouser&sku=710-61300211121&country=DE&channel=BOM%20Report) | 1 | 0,13
J_A1 | 61300211121 |  |  | 2Pol; gerade; WR-PHD 2.54 mm THT Pin Header | 1 | YES | NO | Mouser | 710-61300211121 | Wurth Electronics | 61300211121 | Mouser | 30823 | 710-61300211121 (https://octopart-clicks.com/click/altium?manufacturer=Wurth%20Electronics&mpn=61300211121&seller=Mouser&sku=710-61300211121&country=DE&channel=BOM%20Report) | 1 | 0,13
J_A2 | 61300211121 |  |  | 2Pol; gerade; WR-PHD 2.54 mm THT Pin Header | 1 | YES | NO | Mouser | 710-61300211121 | Wurth Electronics | 61300211121 | Mouser | 30823 | 710-61300211121 (https://octopart-clicks.com/click/altium?manufacturer=Wurth%20Electronics&mpn=61300211121&seller=Mouser&sku=710-61300211121&country=DE&channel=BOM%20Report) | 1 | 0,13
J_B1 | 61300211121 |  |  | 2Pol; gerade; WR-PHD 2.54 mm THT Pin Header | 1 | YES | NO | Mouser | 710-61300211121 | Wurth Electronics | 61300211121 | Mouser | 30823 | 710-61300211121 (https://octopart-clicks.com/click/altium?manufacturer=Wurth%20Electronics&mpn=61300211121&seller=Mouser&sku=710-61300211121&country=DE&channel=BOM%20Report) | 1 | 0,13
J_B2 | 61300211121 |  |  | 2Pol; gerade; WR-PHD 2.54 mm THT Pin Header | 1 | YES | NO | Mouser | 710-61300211121 | Wurth Electronics | 61300211121 | Mouser | 30823 | 710-61300211121 (https://octopart-clicks.com/click/altium?manufacturer=Wurth%20Electronics&mpn=61300211121&seller=Mouser&sku=710-61300211121&country=DE&channel=BOM%20Report) | 1 | 0,13
J_C1 | 61300211121 |  |  | 2Pol; gerade; WR-PHD 2.54 mm THT Pin Header | 1 | YES | NO | Mouser | 710-61300211121 | Wurth Electronics | 61300211121 | Mouser | 30823 | 710-61300211121 (https://octopart-clicks.com/click/altium?manufacturer=Wurth%20Electronics&mpn=61300211121&seller=Mouser&sku=710-61300211121&country=DE&channel=BOM%20Report) | 1 | 0,13
J_C2 | 61300211121 |  |  | 2Pol; gerade; WR-PHD 2.54 mm THT Pin Header | 1 | YES | NO | Mouser | 710-61300211121 | Wurth Electronics | 61300211121 | Mouser | 30823 | 710-61300211121 (https://octopart-clicks.com/click/altium?manufacturer=Wurth%20Electronics&mpn=61300211121&seller=Mouser&sku=710-61300211121&country=DE&channel=BOM%20Report) | 1 | 0,13
J_D1 | 61300211121 |  |  | 2Pol; gerade; WR-PHD 2.54 mm THT Pin Header | 1 | YES | NO | Mouser | 710-61300211121 | Wurth Electronics | 61300211121 | Mouser | 30823 | 710-61300211121 (https://octopart-clicks.com/click/altium?manufacturer=Wurth%20Electronics&mpn=61300211121&seller=Mouser&sku=710-61300211121&country=DE&channel=BOM%20Report) | 1 | 0,13
J_D2 | 61300211121 |  |  | 2Pol; gerade; WR-PHD 2.54 mm THT Pin Header | 1 | YES | NO | Mouser | 710-61300211121 | Wurth Electronics | 61300211121 | Mouser | 30823 | 710-61300211121 (https://octopart-clicks.com/click/altium?manufacturer=Wurth%20Electronics&mpn=61300211121&seller=Mouser&sku=710-61300211121&country=DE&channel=BOM%20Report) | 1 | 0,13
J_E1 | 61300211121 |  |  | 2Pol; gerade; WR-PHD 2.54 mm THT Pin Header | 1 | YES | NO | Mouser | 710-61300211121 | Wurth Electronics | 61300211121 | Mouser | 30823 | 710-61300211121 (https://octopart-clicks.com/click/altium?manufacturer=Wurth%20Electronics&mpn=61300211121&seller=Mouser&sku=710-61300211121&country=DE&channel=BOM%20Report) | 1 | 0,13
J_E2 | 61300211121 |  |  | 2Pol; gerade; WR-PHD 2.54 mm THT Pin Header | 1 | YES | NO | Mouser | 710-61300211121 | Wurth Electronics | 61300211121 | Mouser | 30823 | 710-61300211121 (https://octopart-clicks.com/click/altium?manufacturer=Wurth%20Electronics&mpn=61300211121&seller=Mouser&sku=710-61300211121&country=DE&channel=BOM%20Report) | 1 | 0,13
C101 | 4,7 µF |  |  | 4,7 µF; 6V; Gr. A; T491A475K006AT | 1 | YES | NO | Digi-Key | 399-9717-1-ND | KEMET | T491A475K006AT | Digi-Key | 1000 | 399-10212-2-ND (https://octopart-clicks.com/click/altium?manufacturer=KEMET&mpn=T491X477K010AT&seller=Digi-Key&sku=399-10212-2-ND&country=DE&channel=BOM%20Report) | 1
C102 | 4,7 µF |  |  | 4,7 µF; 6V; Gr. A; T491A475K006AT | 1 | YES | NO | Digi-Key | 399-9717-1-ND | KEMET | T491A475K006AT | Digi-Key | 1000 | 399-10212-2-ND (https://octopart-clicks.com/click/altium?manufacturer=KEMET&mpn=T491X477K010AT&seller=Digi-Key&sku=399-10212-2-ND&country=DE&channel=BOM%20Report) | 1
C104 | 4,7 µF |  |  | 4,7 µF; 6V; Gr. A; T491A475K006AT | 1 | YES | NO | Digi-Key | 399-9717-1-ND | KEMET | T491A475K006AT | Digi-Key | 1000 | 399-10212-2-ND (https://octopart-clicks.com/click/altium?manufacturer=KEMET&mpn=T491X477K010AT&seller=Digi-Key&sku=399-10212-2-ND&country=DE&channel=BOM%20Report) | 1
C105 | 4,7 µF |  |  | 4,7 µF; 6V; Gr. A; T491A475K006AT | 1 | YES | NO | Digi-Key | 399-9717-1-ND | KEMET | T491A475K006AT | Digi-Key | 1000 | 399-10212-2-ND (https://octopart-clicks.com/click/altium?manufacturer=KEMET&mpn=T491X477K010AT&seller=Digi-Key&sku=399-10212-2-ND&country=DE&channel=BOM%20Report) | 1
C100 | 10 µF |  |  | 10 µF, 35V, 125 mOhm, Gr. Dpartnumb: T495D106K035ATE125 | 1 | YES | NO | Digi-Key | 399-10292-1-ND | KEMET | T495D106K035ATE125 | Mouser | 607 | 80-T495D106K35ATE125 (https://octopart-clicks.com/click/altium?manufacturer=KEMET&mpn=T495D106K035ATE125&seller=Mouser&sku=80-T495D106K35ATE125&country=DE&channel=BOM%20Report) | 1 | 1,65
U101 | LM1117IMP-3.3/NOPB |  |  | 800mA Low-Dropout Linear Regulator, 4-pin SOT-223, Pb-Free | 1 | YES | NO |  |  | Texas Instruments | LM1117IMP-3.3/NOPB | RSComponents | 3890 | 1977196 (https://octopart-clicks.com/click/altium?manufacturer=Texas%20Instruments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) | 1
U102 | LM1117IMP-5.0/NOPB |  |  | 800mA Low-Dropout Linear Regulator, 4-pin SOT-223, Pb-Free | 1 | YES | NO |  |  | Texas Instruments | LM1117IMP-5.0/NOPB | RSComponents | 2480 | 5358641P (https://octopart-clicks.com/click/altium?manufacturer=TI%20National%20Semiconductor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) | 1
R1_A | 10k |  |  | 0805 Yageo Standard BlackBox Resistors | 1 | YES | NO |  |  | Yageo
R1_B | 10k |  |  | 0805 Yageo Standard BlackBox Resistors | 1 | YES | NO |  |  | Yageo
R1_C | 10k |  |  | 0805 Yageo Standard BlackBox Resistors | 1 | YES | NO |  |  | Yageo
R1_D | 10k |  |  | 0805 Yageo Standard BlackBox Resistors | 1 | YES | NO |  |  | Yageo
R1_E | 10k |  |  | 0805 Yageo Standard BlackBox Resistors | 1 | YES | NO |  |  | Yageo
R2_A | 10k |  |  | 0805 Yageo Standard BlackBox Resistors | 1 | YES | NO |  |  | Yageo
R2_B | 10k |  |  | 0805 Yageo Standard BlackBox Resistors | 1 | YES | NO |  |  | Yageo
R2_C | 10k |  |  | 0805 Yageo Standard BlackBox Resistors | 1 | YES | NO |  |  | Yageo
R2_D | 10k |  |  | 0805 Yageo Standard BlackBox Resistors | 1 | YES | NO |  |  | Yageo
R2_E | 10k |  |  | 0805 Yageo Standard BlackBox Resistors | 1 | YES | NO |  |  | Yageo
R3_A | 10k |  |  | 0805 Yageo Standard BlackBox Resistors | 1 | YES | NO |  |  | Yageo
R3_B | 10k |  |  | 0805 Yageo Standard BlackBox Resistors | 1 | YES | NO |  |  | Yageo
R4_A | 10k |  |  | 0805 Yageo Standard BlackBox Resistors | 1 | YES | NO |  |  | Yageo
R4_B | 10k |  |  | 0805 Yageo Standard BlackBox Resistors | 1 | YES | NO |  |  | Yageo
R5_A | 0 |  |  | 0805 Yageo Standard BlackBox Resistors | 1 | YES | NO |  |  | Yageo
R5_B | 0 |  |  | 0805 Yageo Standard BlackBox Resistors | 1 | YES | NO |  |  | Yageo
R6_A | open |  |  | 0805 Yageo Standard BlackBox Resistors | 1 | YES | NO |  |  | Yageo
R6_B | open |  |  | 0805 Yageo Standard BlackBox Resistors | 1 | YES | NO |  |  | Yageo
R7_A | open |  |  | 0805 Yageo Standard BlackBox Resistors | 1 | YES | NO |  |  | Yageo
R7_B | open |  |  | 0805 Yageo Standard BlackBox Resistors | 1 | YES | NO |  |  | Yageo
R8 | 1k |  |  | 0805 Yageo Standard BlackBox Resistors | 1 | YES | NO |  |  | Yageo
R9 | 560 |  |  | 0805 Yageo Standard BlackBox Resistors | 1 | YES | NO |  |  | Yageo
R10 | 27 |  |  | 0805 Yageo Standard BlackBox Resistors | 1 | YES | NO |  |  | Yageo
R11 | 1k8 |  |  | 0805 Yageo Standard BlackBox Resistors | 1 | YES | NO |  |  | Yageo
R12 | 470 |  |  | 0805 Yageo Standard BlackBox Resistors | 1 | YES | NO |  |  | Yageo
R13 | 150 |  |  | 0805 Yageo Standard BlackBox Resistors | 1 | YES | NO |  |  | Yageo
R14 | 10 |  |  | 0805 Yageo Standard BlackBox Resistors | 1 | YES | NO |  |  | Yageo
C2_A | 1uF |  |  | CAP CER 1UF 10V X7R 1206 | 1 | YES | NO | Digi-Key | 732-7685-1-ND | Wurth Electronics Inc. | 885012208013 | Mouser | 2825 | 710-885012208013 (https://octopart-clicks.com/click/altium?manufacturer=Wurth%20Electronics&mpn=885012208013&seller=Mouser&sku=710-885012208013&country=DE&channel=BOM%20Report) | 1 | 0,16
C2_B | 1uF |  |  | CAP CER 1UF 10V X7R 1206 | 1 | YES | NO | Digi-Key | 732-7685-1-ND | Wurth Electronics Inc. | 885012208013 | Mouser | 2825 | 710-885012208013 (https://octopart-clicks.com/click/altium?manufacturer=Wurth%20Electronics&mpn=885012208013&seller=Mouser&sku=710-885012208013&country=DE&channel=BOM%20Report) | 1 | 0,16
C1_A | 2.2uF |  |  | CAP CER 2.2UF 10V X7R 1206 | 1 | YES | NO | Mouser | 710-885012208015 | Wurth Electronics | 885012208015 | Mouser | 2813 | 710-885012208015 (https://octopart-clicks.com/click/altium?manufacturer=Wurth%20Electronics&mpn=885012208015&seller=Mouser&sku=710-885012208015&country=DE&channel=BOM%20Report) | 1 | 0,35
C1_B | 2.2uF |  |  | CAP CER 2.2UF 10V X7R 1206 | 1 | YES | NO | Mouser | 710-885012208015 | Wurth Electronics | 885012208015 | Mouser | 2813 | 710-885012208015 (https://octopart-clicks.com/click/altium?manufacturer=Wurth%20Electronics&mpn=885012208015&seller=Mouser&sku=710-885012208015&country=DE&channel=BOM%20Report) | 1 | 0,35
C3_A | 100nF |  |  | generic 0805 COG oder X7R Vielschichtkondensatoren max. +/-10% | 1 | YES | NO
C3_B | 100nF |  |  | generic 0805 COG oder X7R Vielschichtkondensatoren max. +/-10% | 1 | YES | NO
C103 | 100nF |  |  | generic 0805 COG oder X7R Vielschichtkondensatoren max. +/-10% | 1 | YES | NO
D1 | LL4007 |  |  | LL4007; Vf 1,1V @ 1A, If = 1A | 1 | YES | NO | Farnell | 2677381 | TAIWAN SEMICONDUCTOR | LL4007G L2 | Farnell | 9863 | 2677381 (https://octopart-clicks.com/click/altium?manufacturer=Taiwan%20Semiconductor&mpn=LL4007G&seller=Farnell&sku=2677381&country=DE&channel=BOM%20Report) | 1
D2 | LL4007 |  |  | LL4007; Vf 1,1V @ 1A, If = 1A | 1 | YES | NO | Farnell | 2677381 | TAIWAN SEMICONDUCTOR | LL4007G L2 | Farnell | 9863 | 2677381 (https://octopart-clicks.com/click/altium?manufacturer=Taiwan%20Semiconductor&mpn=LL4007G&seller=Farnell&sku=2677381&country=DE&channel=BOM%20Report) | 1
U100 | LM317LM |  |  | LM317LM/NOPB; 8PIN SOIC; 0,1A | 1 | YES | NO | Mouser | 926-LM317LM/NOPB | Texas Instruments | LM317LM/NOPB | Mouser | 21483 | 926-LM317LMX/NOPB (https://octopart-clicks.com/click/altium?manufacturer=TI%20National%20Semiconductor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) | 1 | 0,8
J1_A | normal solderbridge |  |  | normal solderbridge | 1 | YES | NO
J1_B | normal solderbridge |  |  | normal solderbridge | 1 | YES | NO
J1_C | normal solderbridge |  |  | normal solderbridge | 1 | YES | NO
J1_D | normal solderbridge |  |  | normal solderbridge | 1 | YES | NO
J1_E | normal solderbridge |  |  | normal solderbridge | 1 | YES | NO
J2_A | normal solderbridge |  |  | normal solderbridge | 1 | YES | NO
J2_B | normal solderbridge |  |  | normal solderbridge | 1 | YES | NO
J2_C | normal solderbridge |  |  | normal solderbridge | 1 | YES | NO
J2_D | normal solderbridge |  |  | normal solderbridge | 1 | YES | NO
J2_E | normal solderbridge |  |  | normal solderbridge | 1 | YES | NO
J3_A | normal solderbridge |  |  | normal solderbridge | 1 | YES | NO
J3_B | normal solderbridge |  |  | normal solderbridge | 1 | YES | NO
J3_C | normal solderbridge |  |  | normal solderbridge | 1 | YES | NO
J3_D | normal solderbridge |  |  | normal solderbridge | 1 | YES | NO
J3_E | normal solderbridge |  |  | normal solderbridge | 1 | YES | NO
J4_A | normal solderbridge |  |  | normal solderbridge | 1 | YES | NO
J4_B | normal solderbridge |  |  | normal solderbridge | 1 | YES | NO
J4_C | normal solderbridge |  |  | normal solderbridge | 1 | YES | NO
J4_D | normal solderbridge |  |  | normal solderbridge | 1 | YES | NO
J4_E | normal solderbridge |  |  | normal solderbridge | 1 | YES | NO
J5_A | normal solderbridge |  |  | normal solderbridge | 1 | YES | NO
J5_B | normal solderbridge |  |  | normal solderbridge | 1 | YES | NO
J5_C | normal solderbridge |  |  | normal solderbridge | 1 | YES | NO
J5_D | normal solderbridge |  |  | normal solderbridge | 1 | YES | NO
J5_E | normal solderbridge |  |  | normal solderbridge | 1 | YES | NO
J6_A | normal solderbridge |  |  | normal solderbridge | 1 | YES | NO
J6_B | normal solderbridge |  |  | normal solderbridge | 1 | YES | NO
J6_C | normal solderbridge |  |  | normal solderbridge | 1 | YES | NO
J6_D | normal solderbridge |  |  | normal solderbridge | 1 | YES | NO
J6_E | normal solderbridge |  |  | normal solderbridge | 1 | YES | NO
J7_A | normal solderbridge |  |  | normal solderbridge | 1 | YES | NO
J7_B | normal solderbridge |  |  | normal solderbridge | 1 | YES | NO
J7_C | normal solderbridge |  |  | normal solderbridge | 1 | YES | NO
J7_D | normal solderbridge |  |  | normal solderbridge | 1 | YES | NO
J7_E | normal solderbridge |  |  | normal solderbridge | 1 | YES | NO
J8_A | normal solderbridge |  |  | normal solderbridge | 1 | YES | NO
J8_B | normal solderbridge |  |  | normal solderbridge | 1 | YES | NO
J8_C | normal solderbridge |  |  | normal solderbridge | 1 | YES | NO
J8_D | normal solderbridge |  |  | normal solderbridge | 1 | YES | NO
J8_E | normal solderbridge |  |  | normal solderbridge | 1 | YES | NO
J10_A | normal solderbridge |  |  | normal solderbridge | 1 | YES | NO
J10_B | normal solderbridge |  |  | normal solderbridge | 1 | YES | NO
J11_A | normal solderbridge |  |  | normal solderbridge | 1 | YES | NO
J11_B | normal solderbridge |  |  | normal solderbridge | 1 | YES | NO
J_12_A | normal solderbridge |  |  | normal solderbridge | 1 | YES | NO
J_12_B | normal solderbridge |  |  | normal solderbridge | 1 | YES | NO
U1_A | SN74LVC1T45DBVT |  |  | Single-Bit Dual-Supply Bus Transceiver with Configurable Voltage Translation and 3-State Outputs, DBV0006A, SMALL T&R | 1 | YES | NO |  |  | Texas Instruments | SN74LVC1T45DBVTG4 | Mouser | 7823 | 595-SN74LVC1T45DBVT (https://octopart-clicks.com/click/altium?manufacturer=Texas%20Instruments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) | 1 | 0,57
U1_B | SN74LVC1T45DBVT |  |  | Single-Bit Dual-Supply Bus Transceiver with Configurable Voltage Translation and 3-State Outputs, DBV0006A, SMALL T&R | 1 | YES | NO |  |  | Texas Instruments | SN74LVC1T45DBVTG4 | Mouser | 7823 | 595-SN74LVC1T45DBVT (https://octopart-clicks.com/click/altium?manufacturer=Texas%20Instruments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) | 1 | 0,57
U1_C | SN74LVC1T45DBVT |  |  | Single-Bit Dual-Supply Bus Transceiver with Configurable Voltage Translation and 3-State Outputs, DBV0006A, SMALL T&R | 1 | YES | NO |  |  | Texas Instruments | SN74LVC1T45DBVTG4 | Mouser | 7823 | 595-SN74LVC1T45DBVT (https://octopart-clicks.com/click/altium?manufacturer=Texas%20Instruments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) | 1 | 0,57
U1_D | SN74LVC1T45DBVT |  |  | Single-Bit Dual-Supply Bus Transceiver with Configurable Voltage Translation and 3-State Outputs, DBV0006A, SMALL T&R | 1 | YES | NO |  |  | Texas Instruments | SN74LVC1T45DBVTG4 | Mouser | 7823 | 595-SN74LVC1T45DBVT (https://octopart-clicks.com/click/altium?manufacturer=Texas%20Instruments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) | 1 | 0,57
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

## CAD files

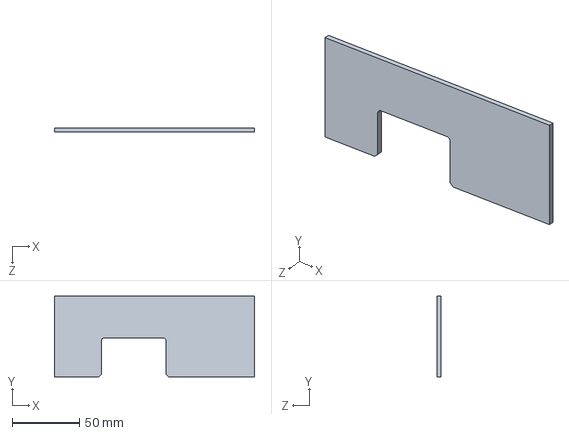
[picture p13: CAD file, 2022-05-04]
Box/CAD_files/Box_side_panel.STEP
149.0 x 60.0 x 3.00 mm

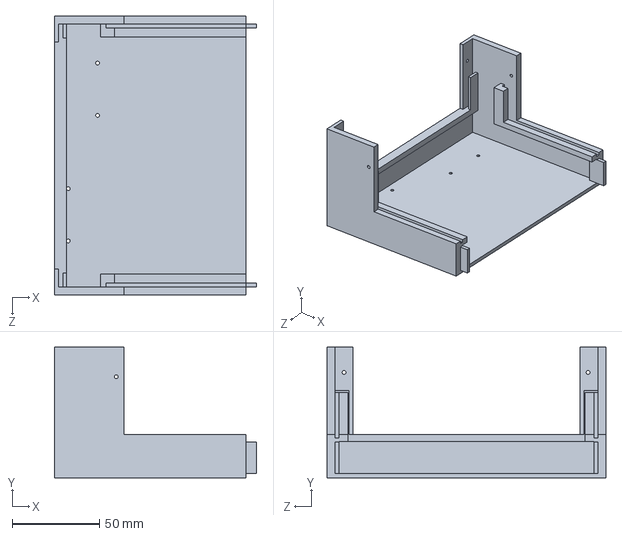
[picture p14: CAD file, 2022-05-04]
Box/CAD_files/Box_part_1.STEP
116.0 x 75.0 x 160.0 mm

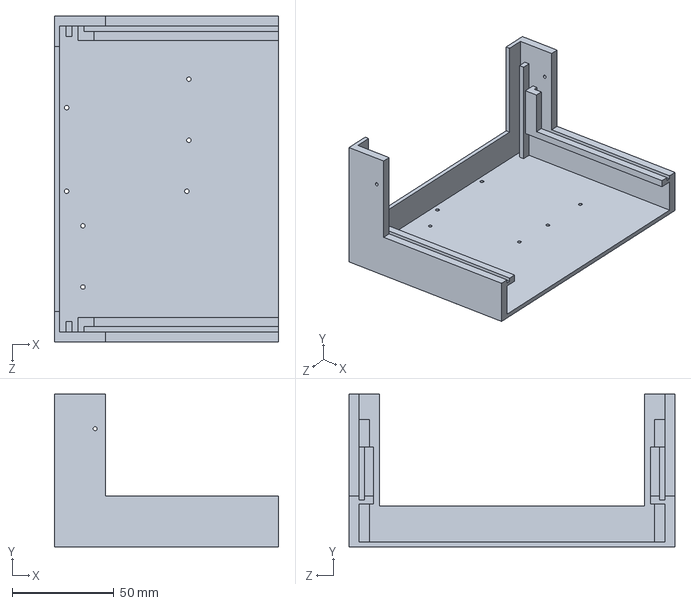
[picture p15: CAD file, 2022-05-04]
Box/CAD_files/Box_part_2.STEP
110.0 x 75.0 x 160.0 mm

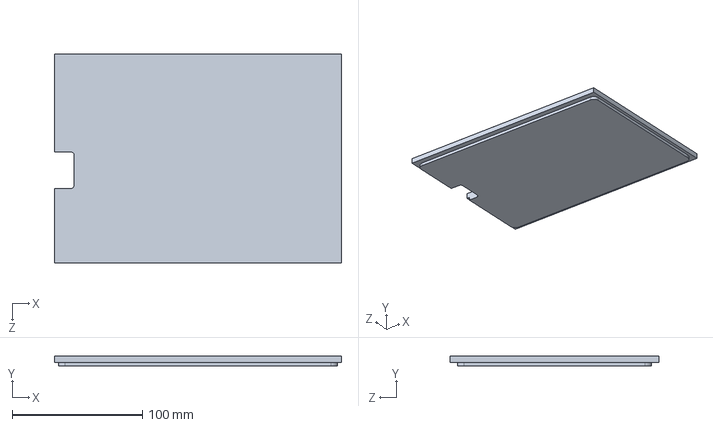
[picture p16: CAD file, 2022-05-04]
Box/CAD_files/Box_lid.STEP
220.0 x 8.00 x 160.0 mm

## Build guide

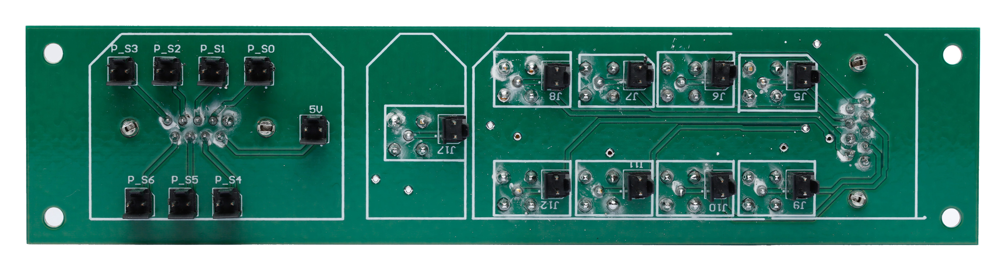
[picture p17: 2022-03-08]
Box_panel_1/Box_panel_1_soldered_back.jpg

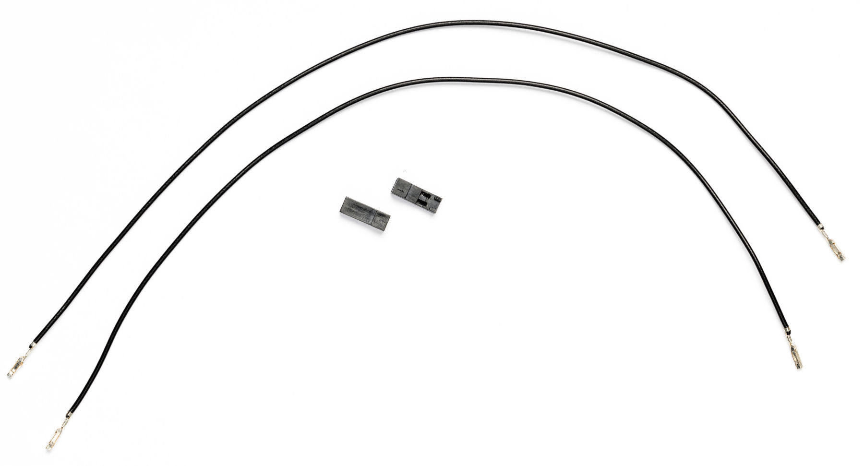
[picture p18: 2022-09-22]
Box/Build_up/01_Cables.jpg

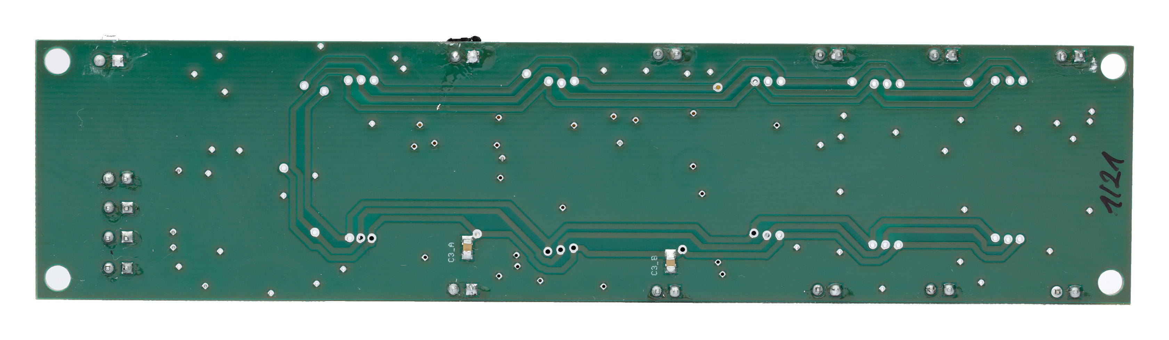
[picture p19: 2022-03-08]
Signal_conversion_board/SCB_soldered_back.jpg

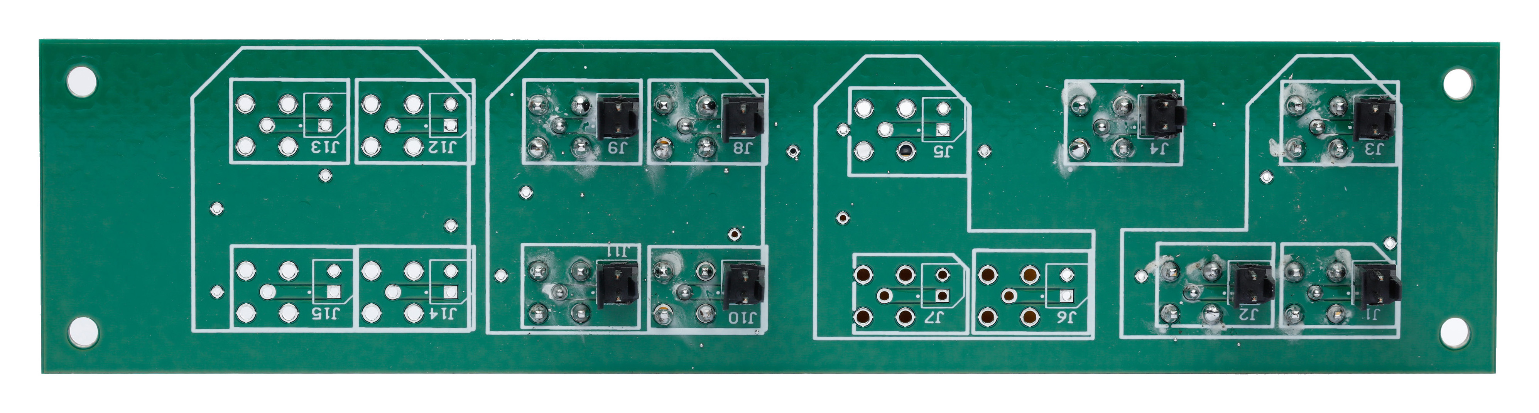
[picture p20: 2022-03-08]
Box_panel_2/Box_panel_2_soldered_back.jpg

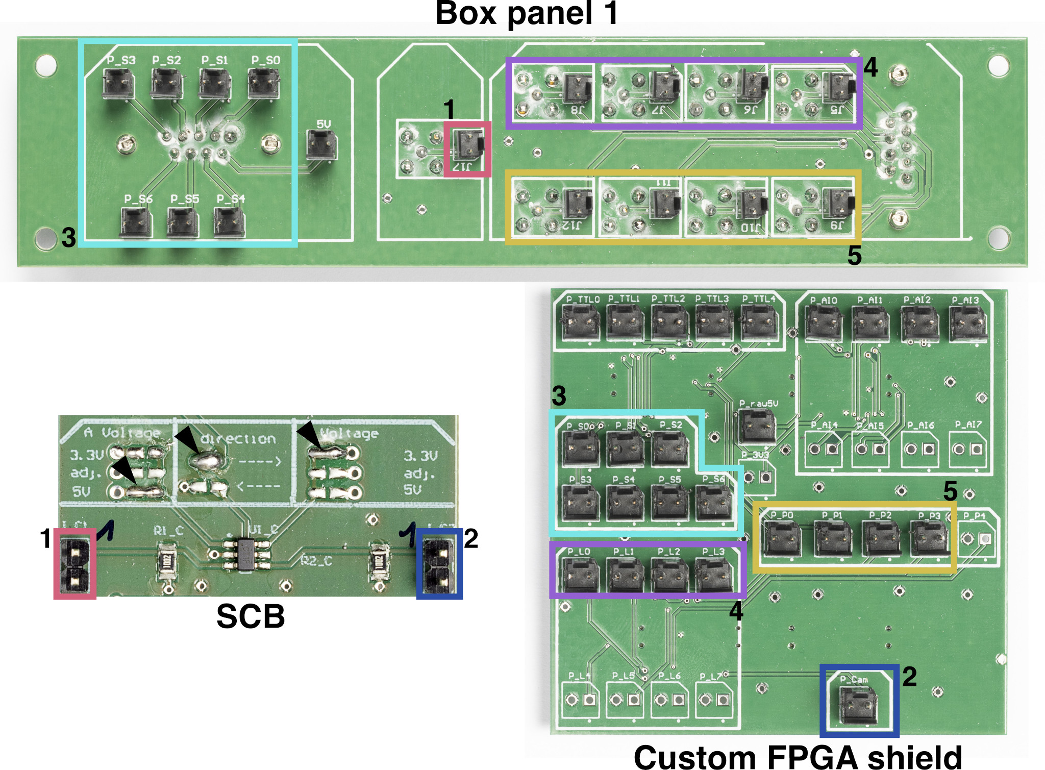
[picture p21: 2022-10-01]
Box/Build_up/07_Wiring_panel_1.jpg

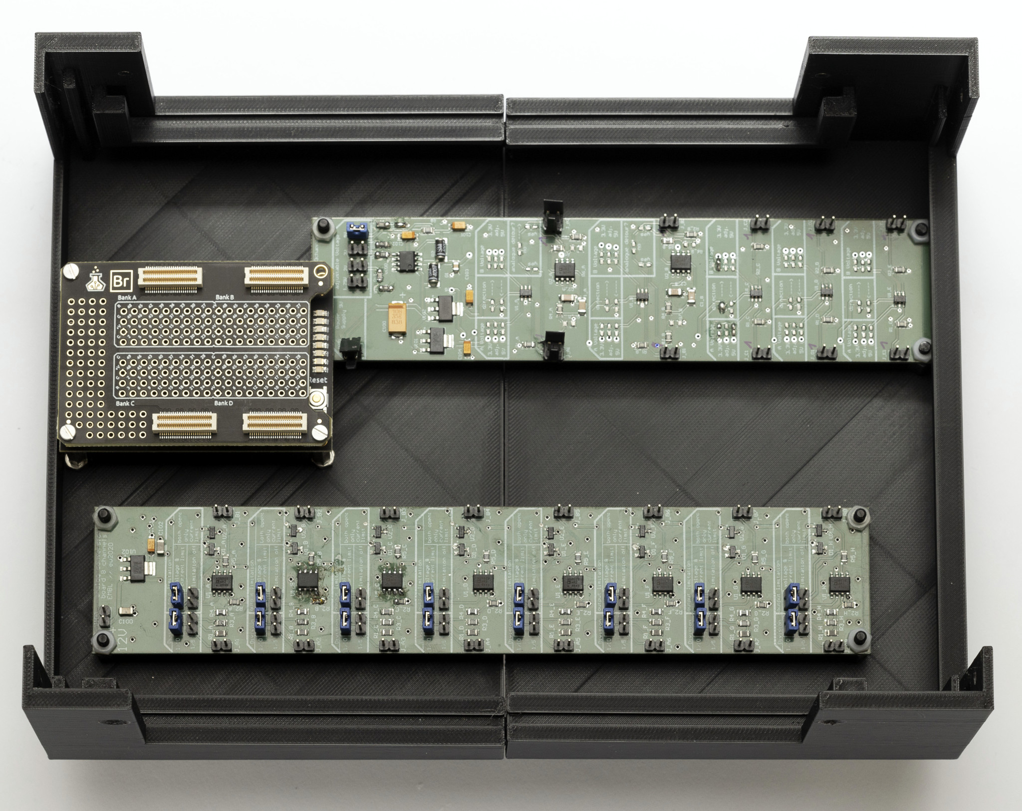
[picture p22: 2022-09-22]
Box/Build_up/04_Boards_mounted.jpg

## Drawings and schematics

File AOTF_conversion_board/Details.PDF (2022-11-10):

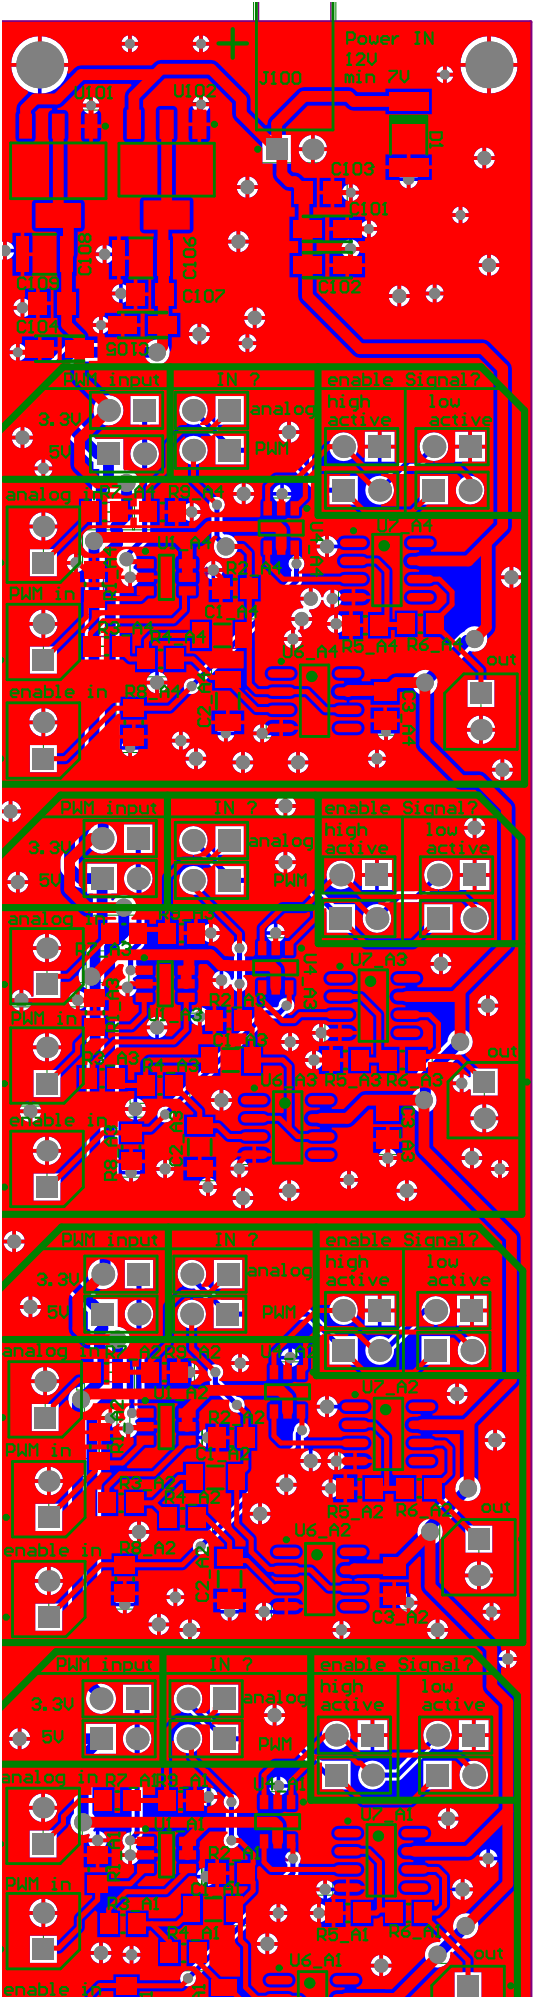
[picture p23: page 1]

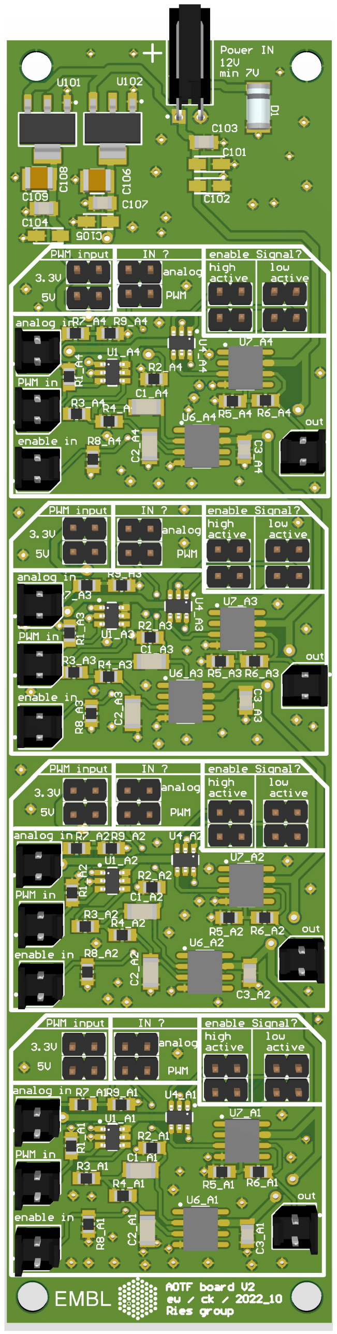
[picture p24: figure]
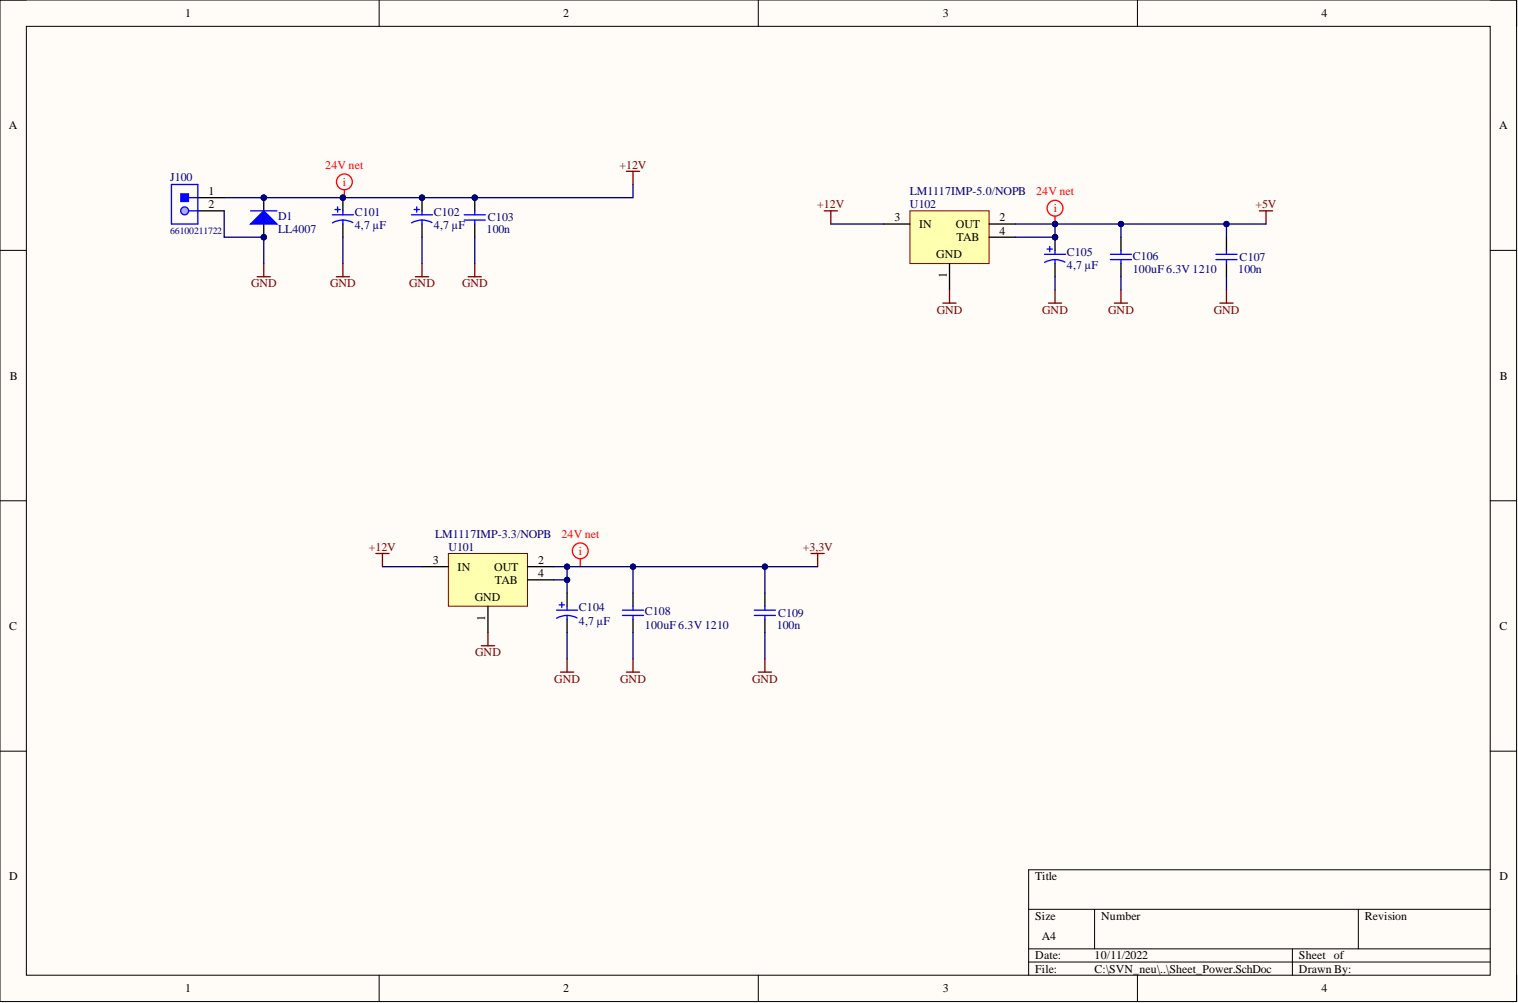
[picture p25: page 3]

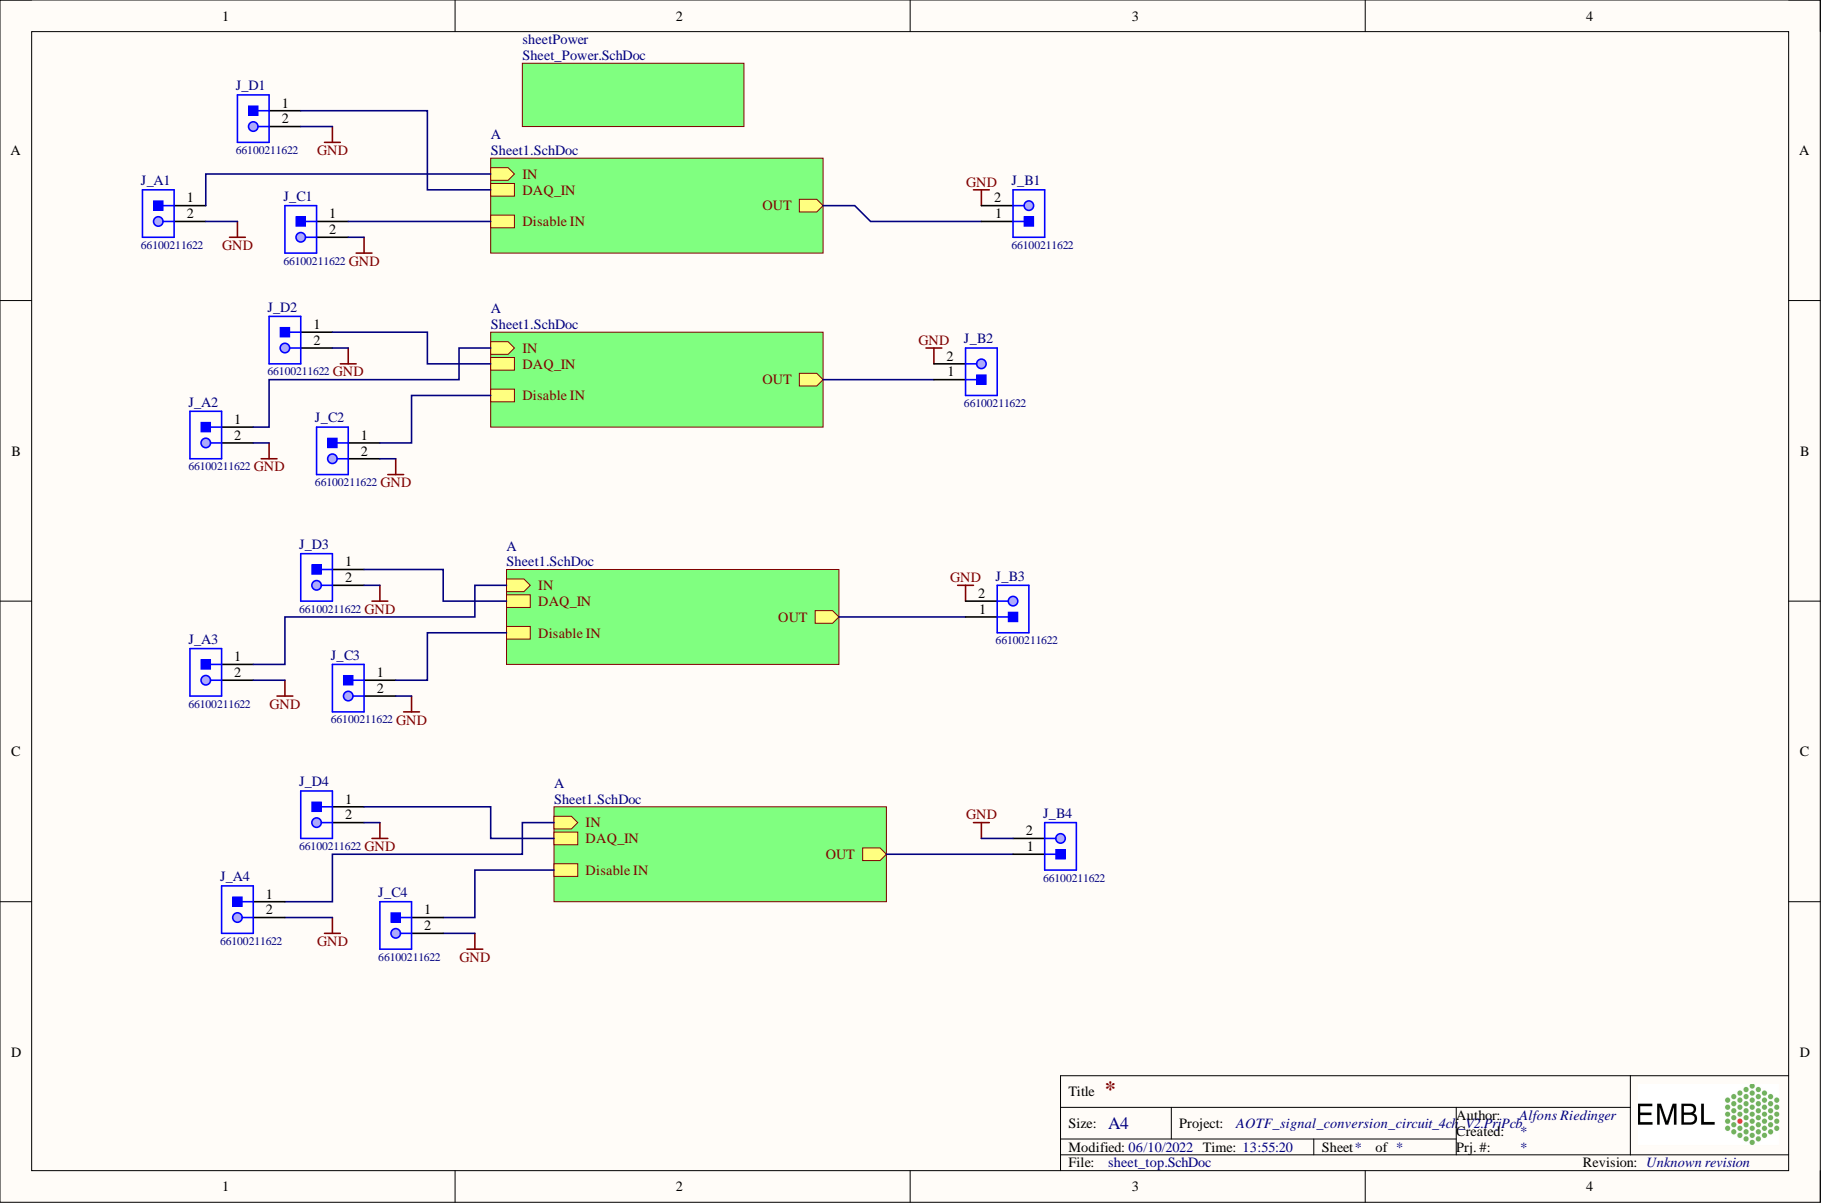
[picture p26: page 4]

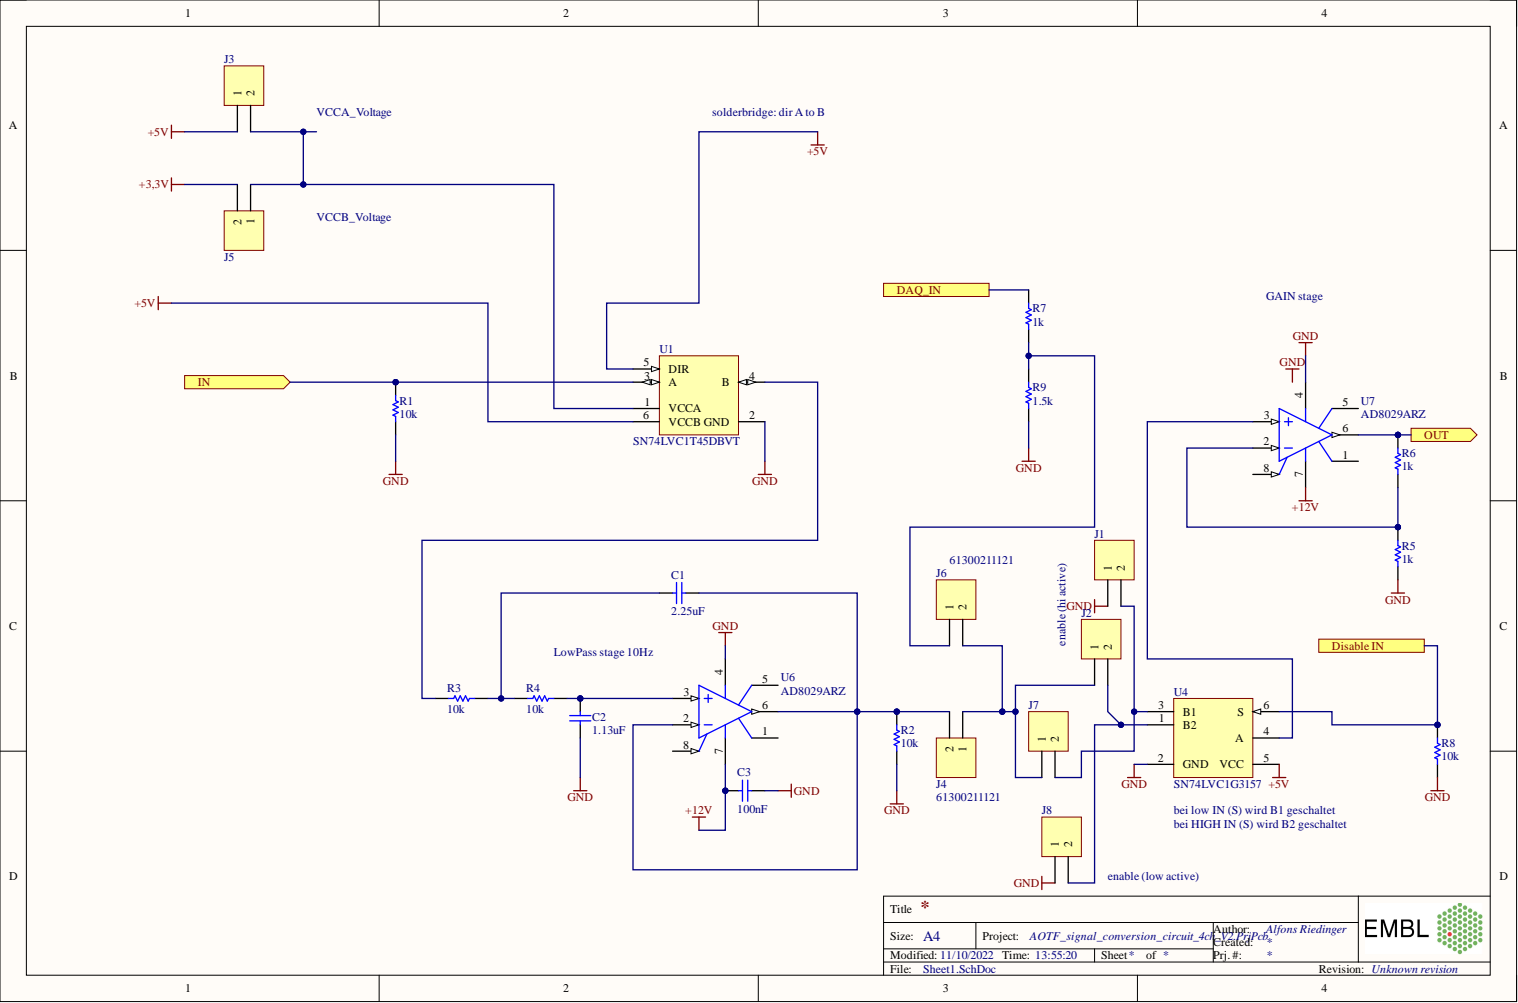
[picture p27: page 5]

VCCB_Voltage

bei low IN (S) wird B1 geschaltet
bei HIGH IN (S) wird B2 geschaltet

enable (low active) GND

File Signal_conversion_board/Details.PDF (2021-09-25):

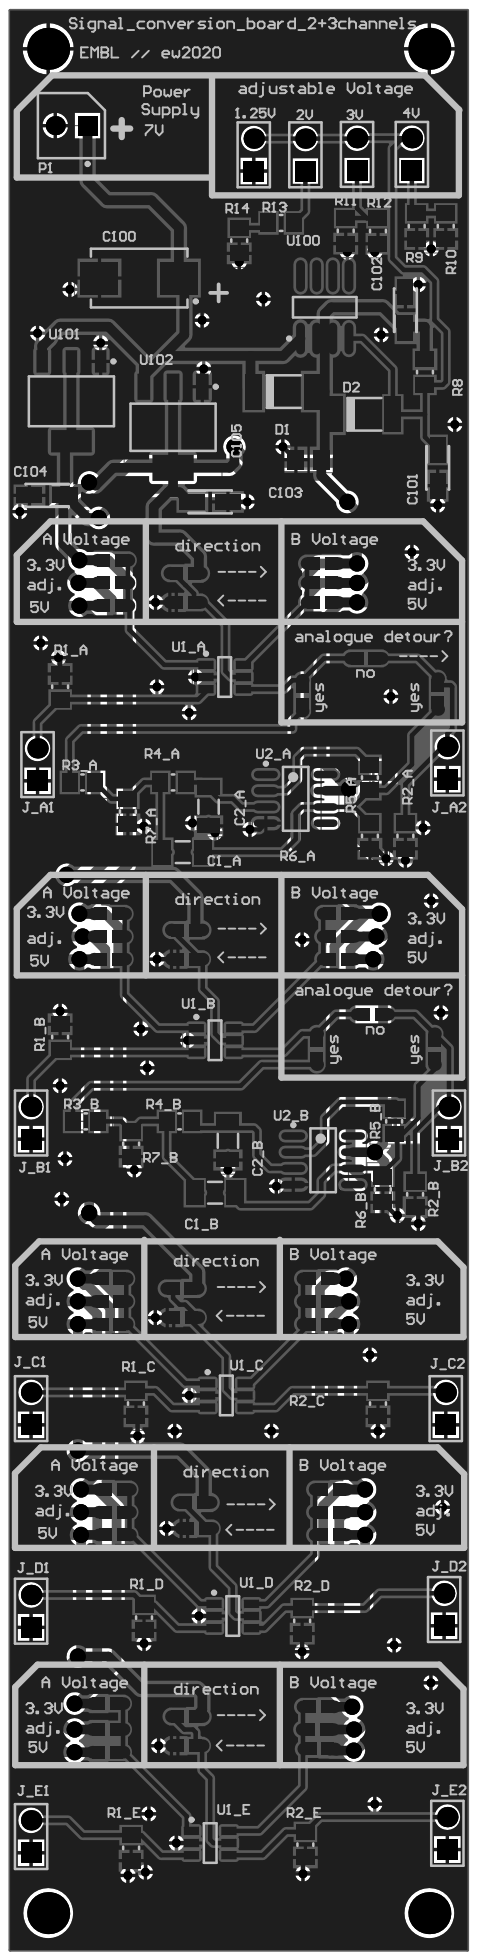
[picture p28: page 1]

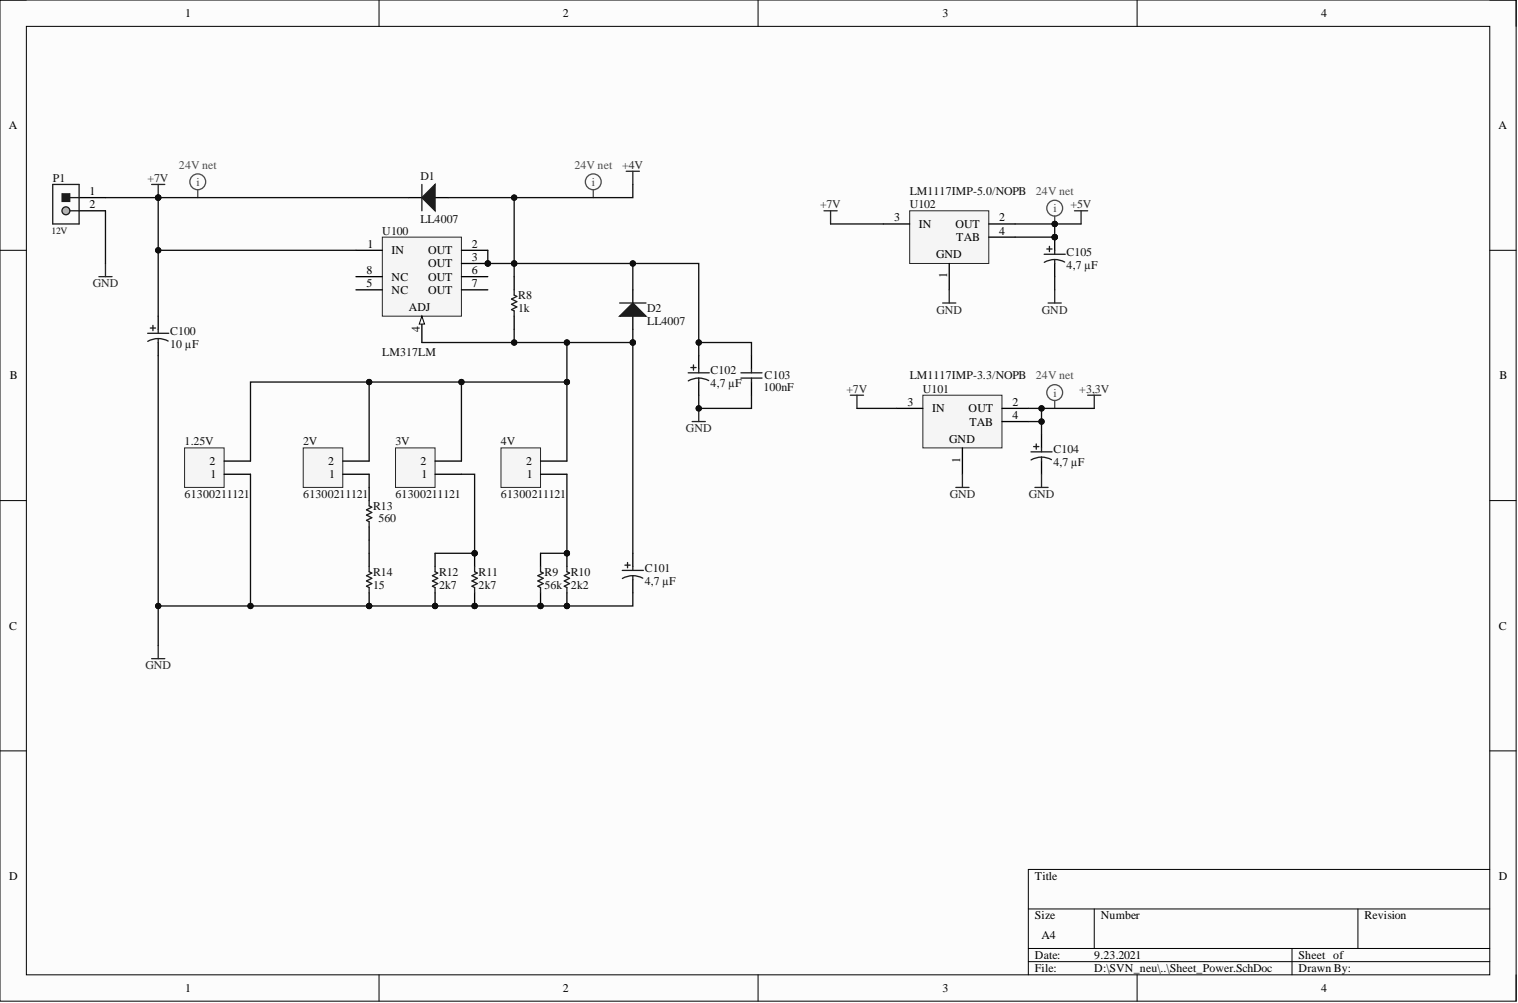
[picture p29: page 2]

N C O U N C O U A D J | T

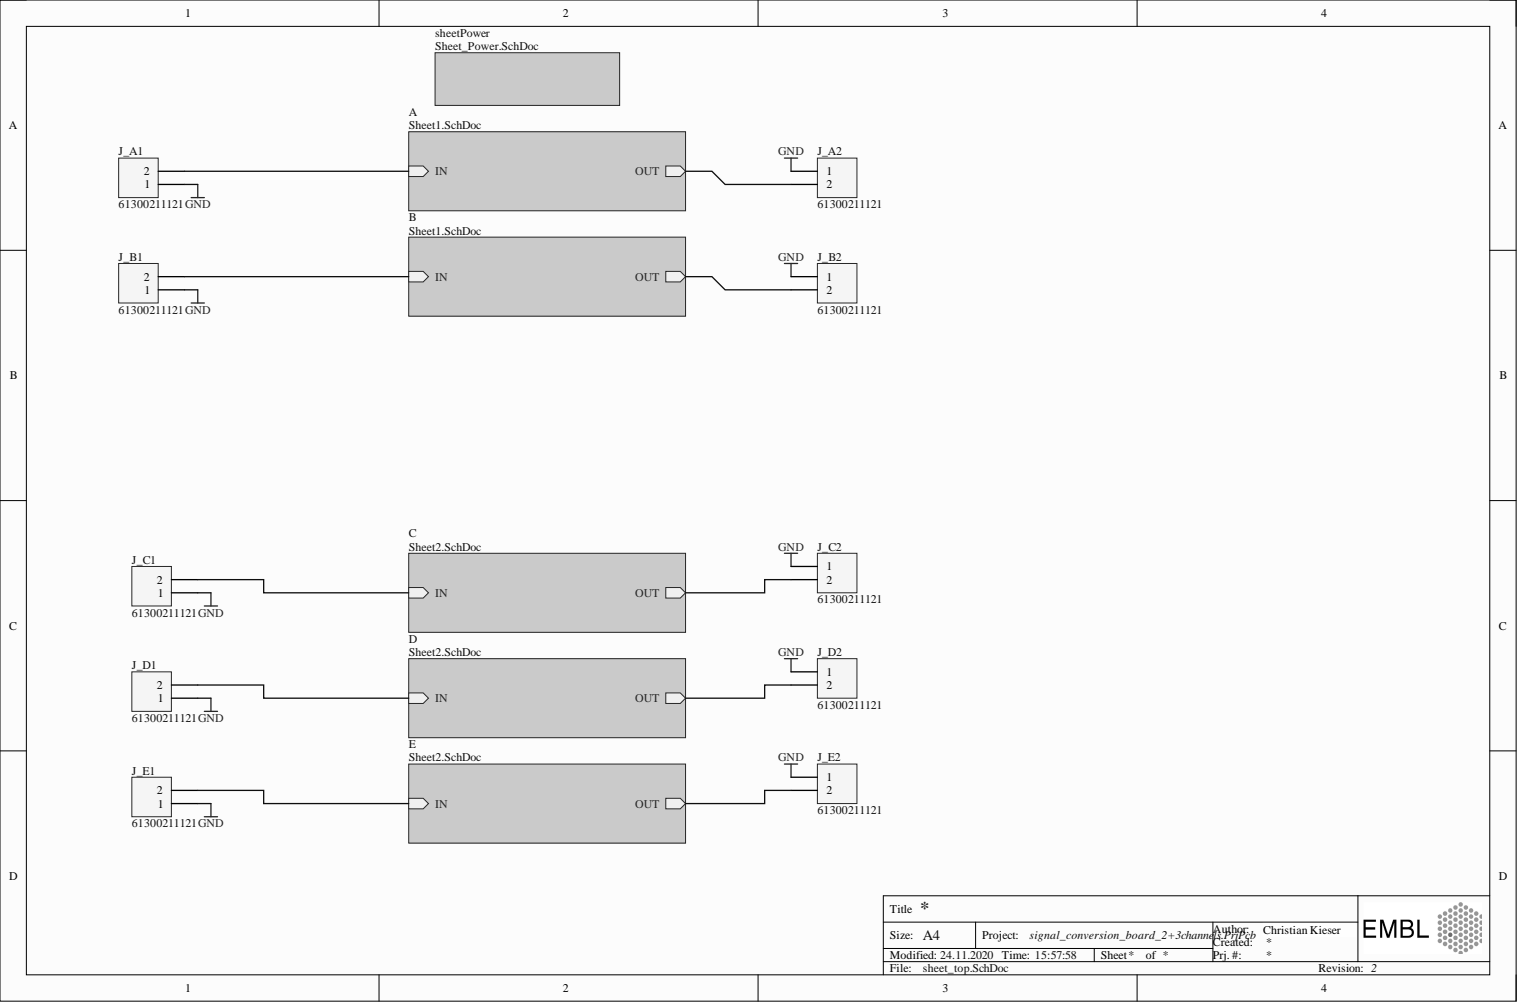
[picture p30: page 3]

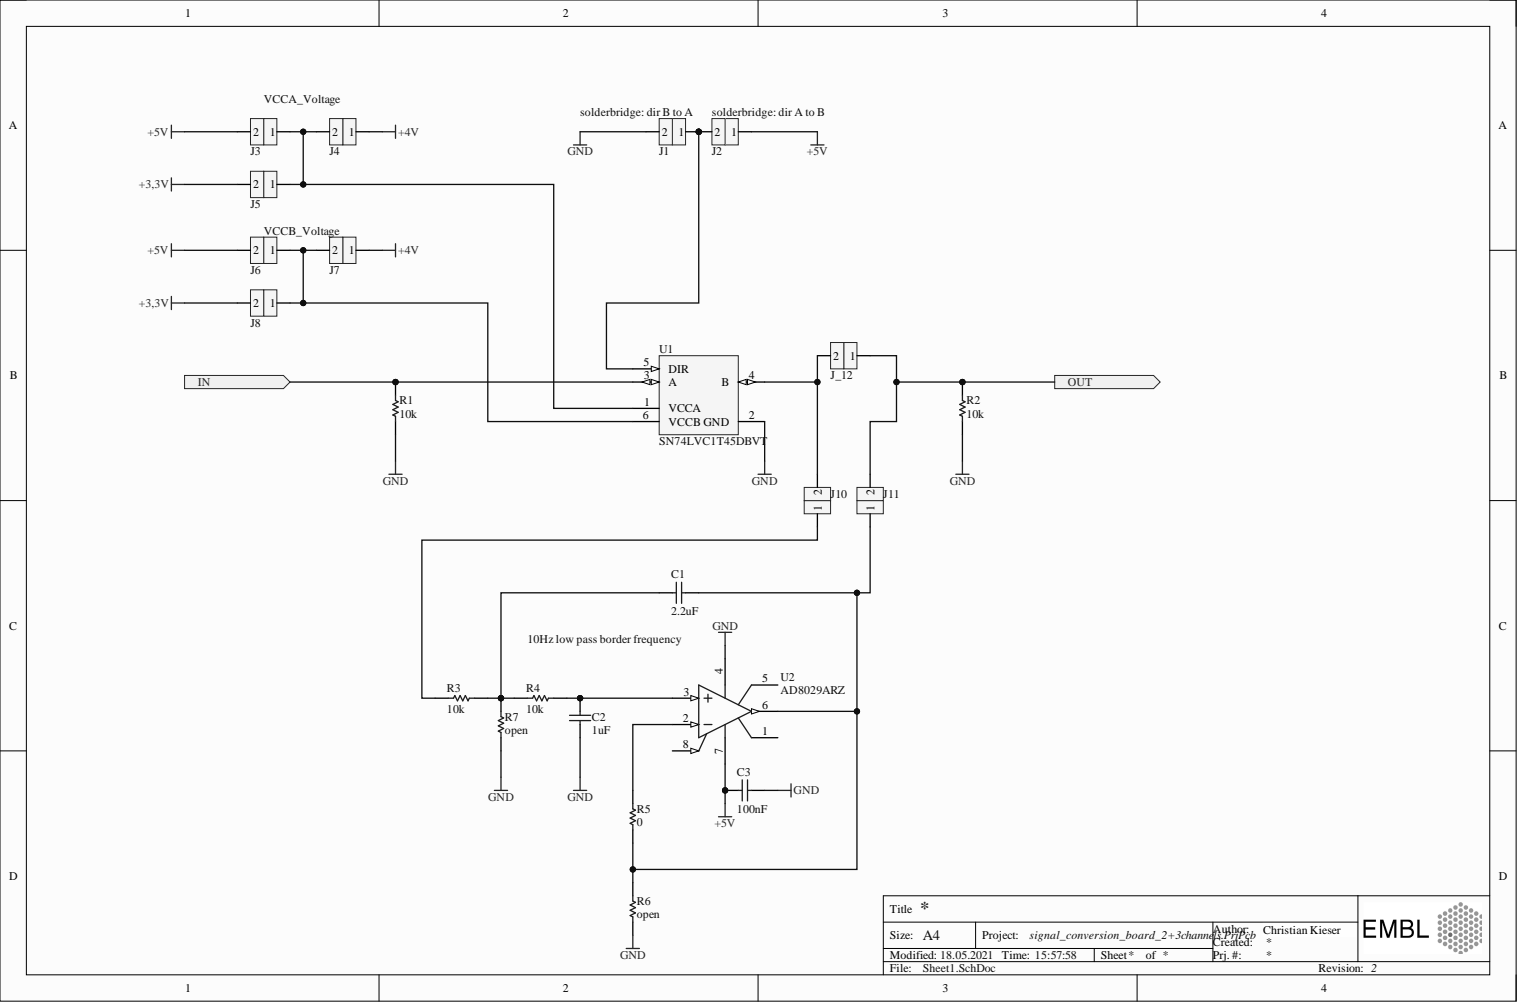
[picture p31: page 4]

A 3 | B | 4 DIR 5

R1 | VCCA 1
10k | | VCCB 6

10Hz low pass border frequency

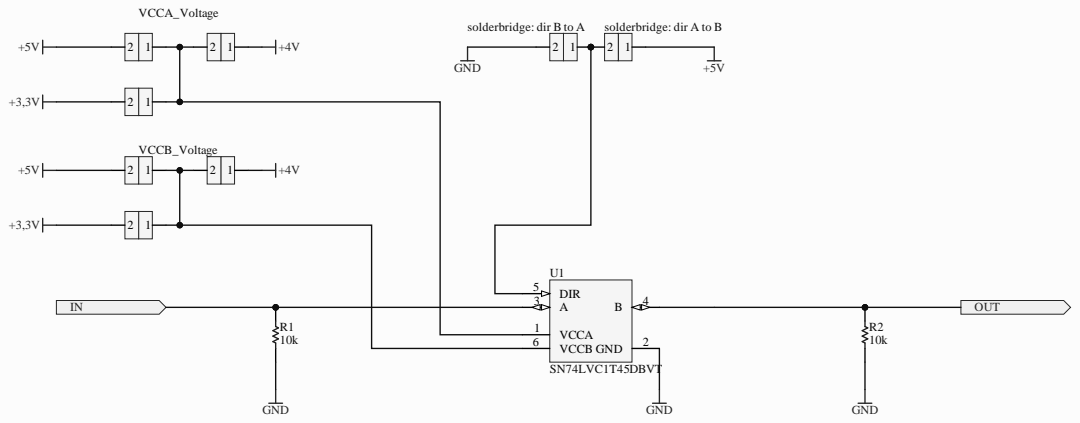
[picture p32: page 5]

A 3 | B | 4 DIR 5

R1 | VCCA 1
10k | VCCB 6

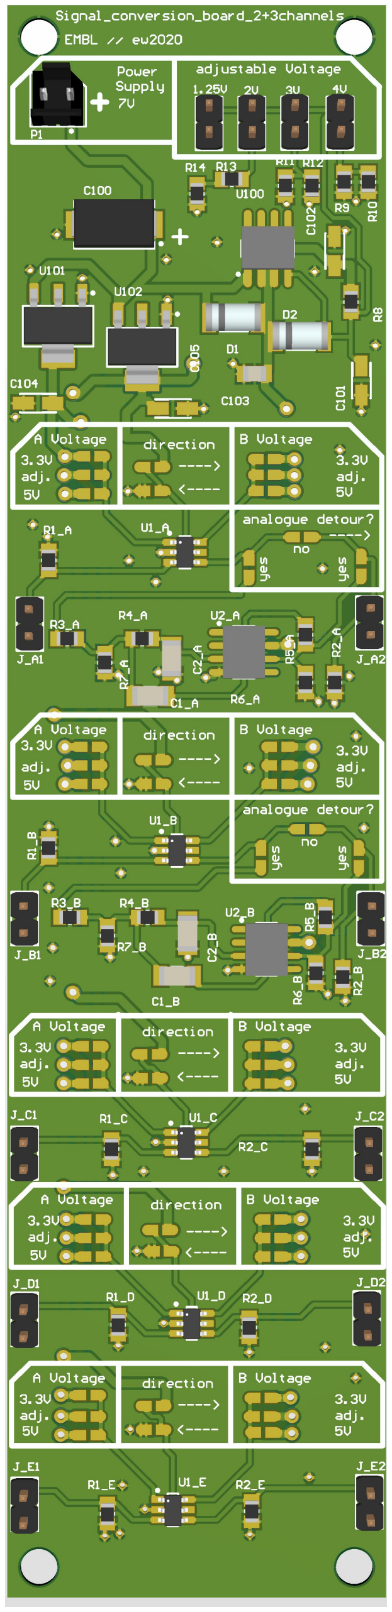
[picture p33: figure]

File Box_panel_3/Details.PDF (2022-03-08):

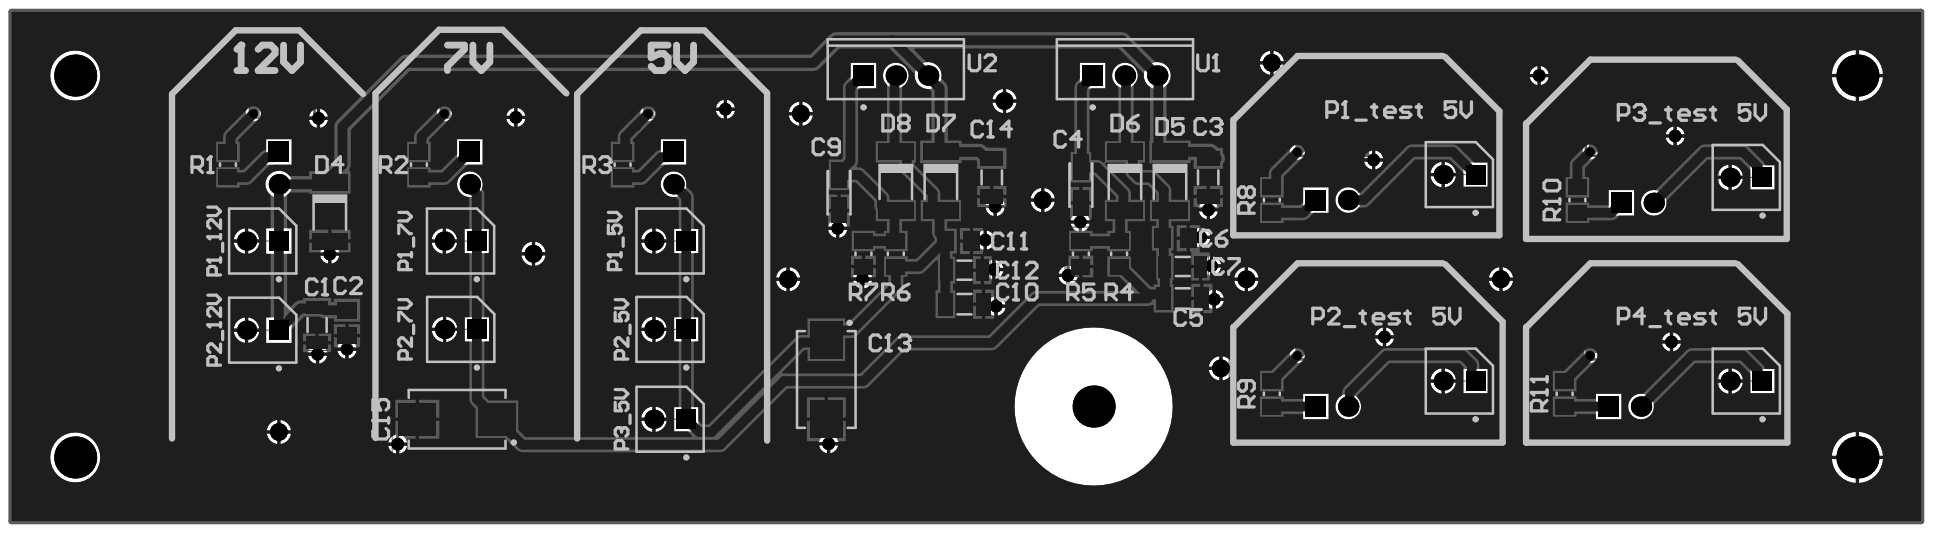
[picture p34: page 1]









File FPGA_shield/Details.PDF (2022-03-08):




AI0_N_23 | AI5_N_28
AI0_P_24 | AI5_P_27






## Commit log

2021-09-25 Add ACB
    [Bill of Materials-BOM1.xlsx, Classes.SchDoc, Sheet1.SchDoc, Sheet_Power.SchDoc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]
2021-09-25 Add SCB
    [Bill of Materials-BOM2.xlsx, Sheet1.SchDoc, Sheet2.SchDoc, Sheet4.SchDoc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]
2021-10-06 Remove link to JobOut file in Altium project
    [analog_conversion_board_8channels.PrjPcb, signal_conversion_board_2+3channels.PrjPcb]
2022-03-08 add Au shield
    [Bill of Materials-BOM1.xlsx, Classes.SchDoc, FPGA_Au_shield.PcbDoc, FPGA_Au_shield.PrjPcb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]
2022-03-08 add box panel 1
    [Bill of Materials-BOM1.xlsx, Classes.SchDoc, FPGA_Au_shield.PcbDoc, FPGA_Au_shield.PrjPcb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]
2022-03-08 add box panel 2
    [Bill of Materials-BOM1.xlsx, Classes.SchDoc, FPGA_Frontpanel_2_V2.PcbDoc, FPGA_Frontpanel_2_V2.PrjPcb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]
2022-03-08 add panel 3
    [Bill of Materials-BOM1.xlsx, Classes.SchDoc, FPGA_Frontpanel_3_V1.PcbDoc, FPGA_Frontpanel_3_V1.PrjPcb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]
2022-03-08 add step by step
    [FPGA_box_parts_list.xlsx]
2022-03-08 renamed shield
    [Bill of Materials-BOM1.xlsx, Classes.SchDoc, FPGA_Au_shield.PcbDoc, FPGA_Au_shield.PrjPcb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]
2022-04-06 add missing files
    [board2.GBL, board2.GBO, board2.GBP, board2.GBS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]
2022-05-04 Add box CAD
    [Box_lid.STEP, Box_part_1.STEP, Box_part_2.STEP, Box_side_panel.STEP]
2022-05-04 update BOM
    [FPGA_box_parts_list.xlsx]
2022-05-04 add SDB
    [Sheet_Power.SchDoc, mainboard.GBL, mainboard.GBO, mainboard.GBP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]
2022-06-13 update box BOM
    [FPGA_box_parts_list.xlsx]
2022-09-22 add build up pics
    [Box_lid.STEP, Box_part_1.STEP, Box_part_2.STEP, Box_side_panel.STEP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]
2022-09-22 add AOTF board
    [AOTF_signal_conversion_circuit_4.PrjPcb, Bill of Materials-AOTF_signal_conversion_circuit_4.xlsx, Sheet1.SchDoc, Sheet2.SchDoc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]
2022-09-22 rename NC drills
2022-10-01 add wiring pictures
2022-11-10 Update AOTF board
    [AOTF_signal_conversion_circuit_4ch_V2.PrjPcb, Bill of Materials-AOTF_signal_conversion_circuit_4.xlsx, Sheet1.SchDoc, Sheet2.SchDoc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]

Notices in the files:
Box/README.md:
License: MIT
